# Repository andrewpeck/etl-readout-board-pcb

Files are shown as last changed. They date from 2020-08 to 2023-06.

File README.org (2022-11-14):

#+OPTIONS: ^:nil
#+EXPORT_EXCLUDE_TAGS: noexport
* CMS ETL Readout Board PCB :TOC:
  - [[#useful-links][Useful Links]]
  - [[#milestones][Milestones]]
  - [[#block-diagrams][Block Diagrams]]
  - [[#mechanical-outline][Mechanical Outline]]
  - [[#power][Power]]
  - [[#lpgbt-configuration][LPGBT Configuration]]
  - [[#vtrx-i2c][VTRX+ I2C]]
  - [[#v2-change-log][v2 Change Log]]
  - [[#errata][Errata]]

** Useful Links
- Documentation page: [[http://etl-rb.docs.cern.ch/][etl-rb.docs.cern.ch]]
- Latest RB Schematics - [[https://gitlab.cern.ch/cms-etl-electronics/readout-board-pcb/uploads/183954f3a47f967752902acf8ae9c3d3/ETL_RB_V1.6.PDF][ETL_RB_V1.6.PDF]]
- Latest RB Gerbers:  [[https://gitlab.cern.ch/cms-etl-electronics/readout-board-pcb/uploads/5678ebf45c38e1c627c98f56c8df58fa/ETL_RB_V1.6.zip][ETL_RB_V1.6.zip]]
- Latest RB Project Archive - [[https://gitlab.cern.ch/cms-etl-electronics/readout-board-pcb/uploads/25dc68e87a1a2c3de5a3411c434b7c02/ETL_RB__11-2-2020_9-17-11_AM_.zip][ETL_RB__11-2-2020_9-17-11_AM_.zip]]
- Mr. Wu's File Stash - [[http://physics.bu.edu/~wusx/download/ETL_RB/]]
- [[https://gitlab.cern.ch/vldbplus/rpi_translator_board_v2/-/raw/master/HW/Project%20Outputs%20for%20RPi_VLDB_Interface/v2-b/SCH/RPi_VLDB_Interface_v2b.PDF?inline=false][PiGBT Schematic]]

- Datasheets:
  + LpGBT Manual - [[https://lpgbt.web.cern.ch/lpgbt/manual/][LpGBT Manual]]
  + GBT-SCA Manual - [[https://espace.cern.ch/GBT-Project/GBT-SCA/Manuals/GBT-SCA_Manual_2019.002.pdf][GBT-SCA Manual]]
  + LINPOL12 Datasheet - [[https://project-dcdc.web.cern.ch/public/Documents/linPOL12V%20datasheetV3.3.pdf][LinPOL12V]]
  + VTRX+ Application Note: [[https://edms.cern.ch/ui/file/2149674/1/VTRxPlusApplicationNote.pdf][VTRxPlusApplicationNote.pdf]]
  + VTRX+ Specification: [[https://edms.cern.ch/ui/file/1719329/1/VTRxPlus_spec_v2.4.pdf][VTRxPlus_spec_v2.4.pdf]]
  + VTRX+ LDD Specs: [[https://edms.cern.ch/ui/file/1719330/1/VLplus_quadLDD_spec_v1.2_prototypes.pdf][VLplus_quadLDD_spec_v1.2_prototypes.pdf]]
- TDR - [[https://cds.cern.ch/record/2667167/files/CMS-TDR-020.pdf][CMS-TDR-020]]
** Milestones
- 2020/11/02 - Finish schematic and layout; Submit files to fab house
- 2020/12/08 - Receive readout boards from Pactron
- 2021/03/01 - Preliminary testing (LPGBT, elinks)
- 2021/03/18 - Working SCA GPIO Control
- 2021/03/23 - Working ADC voltage readings
- 2021/05/11 - 2nd batch of readout boards delivered to BU
- 2021/05/19 - Working SCA I2C master
** Block Diagrams
*** Data Flow
#+ATTR_HTML: :width 700px
[[file:docs/data-flow.svg]]
*** Module Connectivity
Full size: [[file:docs/module-connectivity.pdf]]
#+ATTR_HTML: :width 700px
[[file:docs/module-connectivity.svg]]
*** Power Distribution
#+ATTR_HTML: :width 700px
[[file:docs/power-distribution.svg]]
*** Control and Monitoring
#+ATTR_HTML: :width 700px
[[file:docs/ctrl-and-mon.svg]]
** Mechanical Outline
#+attr_org: :width 700px
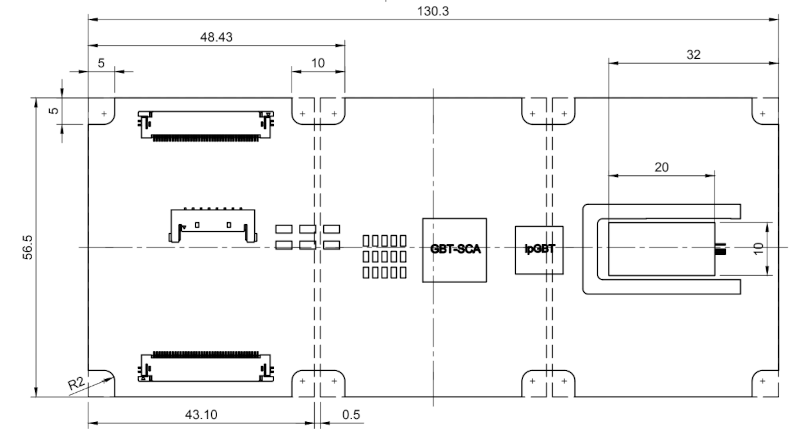
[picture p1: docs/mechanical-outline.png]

** Power
*** Power Estimates

The readout board is expected to dissipate up to ~1.3W, along with some
additional power for LINPOL conversion efficiency. Total power should be around
2W. Details of the calculation follow.

*NOTE:* This calculation is for a configuration of *2tx + 1rx* (i.e. with a trigger
path). The numbers are different if this is not the case (subtract roughly 0.6W
for the LPGBT/VTRX).

|-----------------------------+------------------|
| Note                        | P (mW)           |
|-----------------------------+------------------|
| 1.2V LPGBT analog + digital | 1000             |
| 1.2V VTRX digital           | 30               |
| 2.5V VTRX analog            | 150 - 175        |
| 1.5V GBT-SCA                | 65.4 - 108       |
| LINPOL12 Loss               | 613 - 853        |
|-----------------------------+------------------|
| *Total*                     | *1858 - 2166 mW* |
|-----------------------------+------------------|

**** VTRX
[[https://edms.cern.ch/ui/file/1719329/1/VTRxPlus_spec_v2.4.pdf][VTRX+ Specification]] specifies:
- A supply current 2V5RX of 40mA
- A supply current 2V5TX of  15/ch @ End of life (30mA for a 2+1 configuration)
- A supply current 1V2D of 5+10/ch mA (25mA for a 2+1 configuration)

|---------+--------+----------------+----------------------------------------|
| Voltage | I (mA) |         P (mW) | Notes                                  |
|---------+--------+----------------+----------------------------------------|
| 2V5RX   |     40 |            100 | 40mA total                             |
| 2V5TX   |  20-30 |          50-75 | 15mA/ch at end of life (10mA to start) |
| 1V2     |     25 |             30 | 5+10mA/ch                              |
|---------+--------+----------------+----------------------------------------|
| *Total* |        | *180 - 205 mW* |                                        |
|---------+--------+----------------+----------------------------------------|

**** GBT-SCA
The GBT-SCA manual specifies power consumption of:

|--------------------------------+-------------------+-----------------|
| Supply                         | Typical (Maximum) | Power mW        |
|--------------------------------+-------------------+-----------------|
| 1V5 VDD core                   | 36 (63) mA        | 54 (94.5) mW    |
| 1V5 AVDD analog                | 0.5 (0.8) mA      | 0.75 (1.2) mW   |
| 1V5 DVDD Static supply current | 7.1 (8.2) mA      | 10.65 (12.3) mW |
|--------------------------------+-------------------+-----------------|
| *Total*                          | *43.6 (72.0) mA*    | *65.4 (108.0) mW* |
|--------------------------------+-------------------+-----------------|

**** LPGBT
LPGBT power measurements can be found at
https://espace.cern.ch/GBT-Project/LpGBT/Presentations/lpGBT20190903.pdf

Note that these numbers may change between v0 and v1 of the LPGBT.

Power consumption is dependent on the exact configuration, but we expect it
should be <500mW

We expect up to 2 LPGBTs per board, so ~1W maximum.

**** LINPOL

Three LINPOL12 chips are used on board to provide 1.5V (GBT-SCA), and 2.5V (1
each for VTRX TX + RX).

For the 2.5V supply a voltage divider is formed by RR0510P-1541-D (1.54k) and
RR0510P-4870-D (487R).
 - V=0.6*(1+1540/487)=2.497V

For the 1.5V supply a voltage divider is formed by RR0510P-6040-D (604R) and
RR0510P-4020-D (402R).
 - V= 0.6*(1+604/402)=1.50V

We have some additional power loss in the LINPOL12 chips, which is dependent on
the exact input voltage. Assuming 8V nominal, we would expect using the /MAXIMUM/
values:

|--------+-------------------------------------------|
| Supply | Power mW                                  |
|--------+-------------------------------------------|
| 1V5    | (8-1.5)*(43.6 - 72) = (283 typ - 468 max) |
| 2V5 TX | (8-2.5)*(20 - 30) = (110 start - 165 EOL) |
| 2V5 RX | (8-2.5)*40 = 220                          |
|--------+-------------------------------------------|
| *Total*  | *613 - 853 mW*                              |
|--------+-------------------------------------------|

** LPGBT Configuration

The DAQ and Trigger LPGBTs are arranged in a master-slave configuration, with
the master LPGBT providing a clock and an I2C bus to the slave.

Both LPGBTs are configured by default in FEC12 10.24 Gbps mode, with jumpers
available to select FEC5 or 5.12 Gbps modes. CHange of the mode affects both
LPGBTs together.

|---------+--------------------------------------------------------|
| Jumpers | Description                                            |
|---------+--------------------------------------------------------|
| JMP1    | Install to set LPGBT MODE[2] to 0 (FEC12 → FEC5)       |
| JMP2    | Install to set LPGBT MODE[3] to 0 (data rate → 5 Gbps) |
|---------+--------------------------------------------------------|

** VTRX+ I2C
VTRX+ documentation does not specify the I2C address of the device, but the
laser driver spec has some details:
[[https://edms.cern.ch/ui/file/1719330/1/VLplus_quadLDD_spec_v1.2_prototypes.pdf]]

I checked the bonding diagram
([[https://edms.cern.ch/ui/file/2146792/1/CERN_VTRxPlus_V10_bonding.pdf]]) and the
address pins are not connected, so they use internal pull down.

The address then is ~0b1010000~ = ~0x50~

** v2 Change Log
- [X] Replace KSC2223 BJT w/ ZXMN2B01FTA
- [X] Parallelized LinPol Outputs for higher output current
- [X] Fix I2C note
- [X] Remove I2C programmer port / EFUSEPOWER
- [X] PB and BV interfaces removed
  - Connections can be made as needed directly on the breakout board
- [X] Addition of LEDs
  + [X] Master and slave READY signals connected to LEDs
  + [X] Connect power to LED
  + [X] Connect LPGBT GPIO to LED
  + [X] Connect SCA GPIO to LED
- [X] lpGBT v1 Changes:
  + [X] SC_I2C changed to BOOTCNF1, Should be tied to 0 (https://lpgbt.web.cern.ch/lpgbt/v1/powerup.html#bootcnf1-bootcnf0)
  + [X] Stateovrd changed to EDINTERM
    - "Notice that pin EDINECTERM contains a pull-down resistor. If left
      unconnected, the eRx termination for the EC channel will be disabled.
      Notice as well, that this pin has no effect when the lpGBT is set to work
      as a transceiver. In that case, it is the responsibility of the user to
      configure the termination for the EC-channel in master lpGBTs."
    - https://lpgbt.web.cern.ch/lpgbt/v1/configuration.html?highlight=edinecterm#ec-channel-control-link-topologies
  + [X] VCOBypass changed to BOOTCNF0
    - https://lpgbt.web.cern.ch/lpgbt/v1/powerup.html#bootcnf1-bootcnf0
    - Need to be able to change from 0 <--> 1 to select boot mode
- [X] Latest module pinout (monitor 1x VREF and VTEMP per ETROC)
- [X] Update module connector (QSE-020-01-F-D)
  + RB side: QSE-020-01-{F,L,C}-D
  + Mating connector QTE-020-01-{F,L,C}-D
  + Test report: https://suddendocs.samtec.com/testreports/168830_report_rev_6_qua.pdf
  + 5mm stack height with QTE lead style -01
  + Catalog page: https://suddendocs.samtec.com/catalog_english/qse.pdf
** Errata
1) KSC2223 footprint is incorrect
   - The footprint of the KSC2223 transistor is incorrect.
2) Incorrect assignment of e-fuse power
   - EFUSEPOWER (2.5V power to be applied only during fusing) is incorrectly
     connected to I2C configuration connector ~P1~, pin 9. Pin 9 is in fact the
     ~MODE3_1V25~ pin of the Rpi control toolkit, and should /not/ be connected to
     EFUSE power.
   - *The trace must be cut*.
3) Erroneous note about I2C addresses
   - The schematic features a note:
#+begin_src
I2C ADDR6, ADDR5 and ADDR4 of ETROC2 must not be all 0 or all 1.
pin 11 of P6, P8 and P10 sets ADDR2 of ETROC2
pin 12 of P6, P8 and P10 sets ADDR3 of ETROC2
#+end_src
     + This note, is, however, a remnant of a previous iteration of the design
       where all modules were on the same i2c bus. In the current configuration,
       each module has its own I2C bus, and shares the same address.

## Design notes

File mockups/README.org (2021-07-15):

* Adapters & Mockup Files
** Power adapter
- [[file:power_adapter/v1_power_adapter.pdf][Schematic]]
- [[file:power_adapter/gerber/v1_power_adapter_gerber_20200714.zip][v1_power_adapter_gerber_20200714.zip]]
#+attr_org: :width 300px
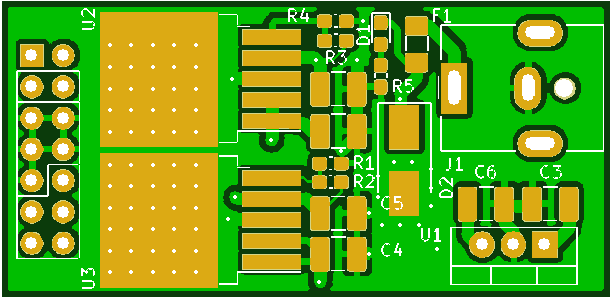
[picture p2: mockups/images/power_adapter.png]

** Emulator Adapter
Adapter board to connect to the ETROC emulator.
- [[file:adapterv1.0.zip][adapterv1.0.zip]]
#+attr_org: :width 500px
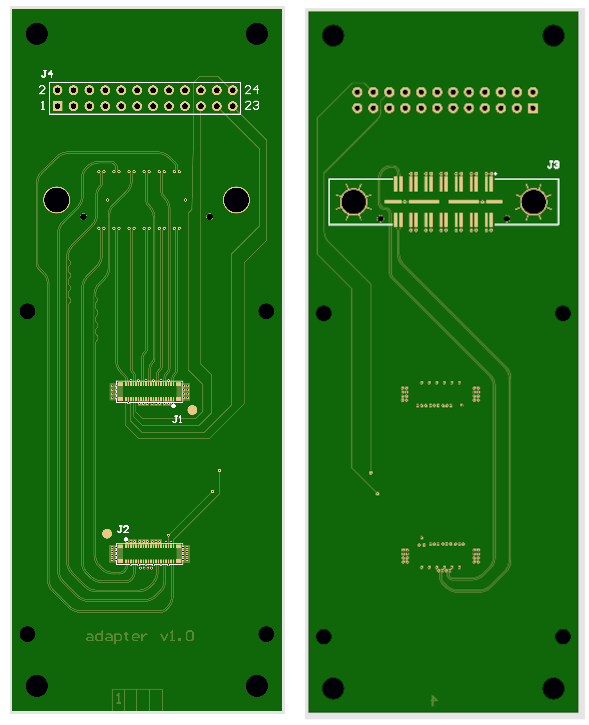
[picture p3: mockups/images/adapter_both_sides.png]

** [[file:ETL_RB_mock1v2.zip][ETL_RB_mock1v2.zip]]
Mockup of a 3 module readout board with realistic pad connectivity
#+attr_org: :width 600px
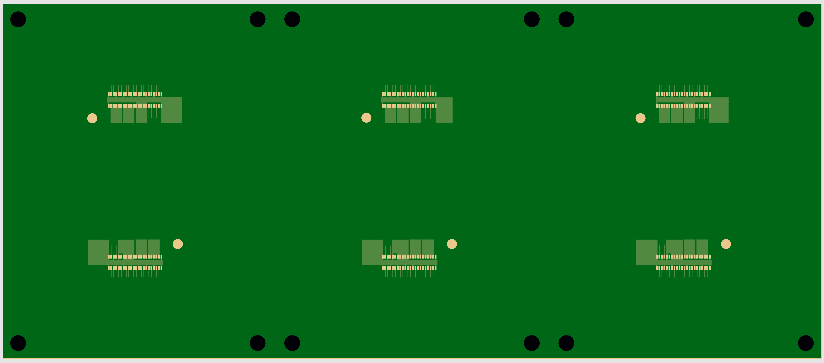
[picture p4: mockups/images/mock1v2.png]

** [[file:ETL_RB_mock2v2.zip][ETL_RB_mock2v2.zip]]
Mockup of a 3 module readout board with daisy-chain connectivity
#+attr_org: :width 600px
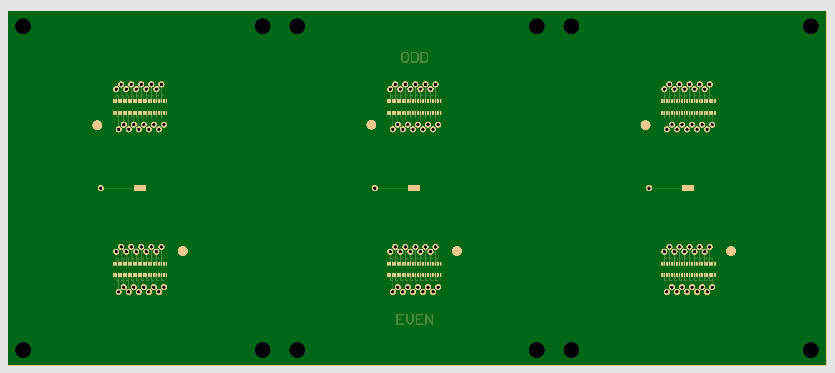
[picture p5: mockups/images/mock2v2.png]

** [[file:module_mockv3.zip][module_mockv3.zip]]
Mockup of a full-sized module (2 sensors, 4 etrocs) with daisy-chain connectivity
#+attr_org: :width 200px
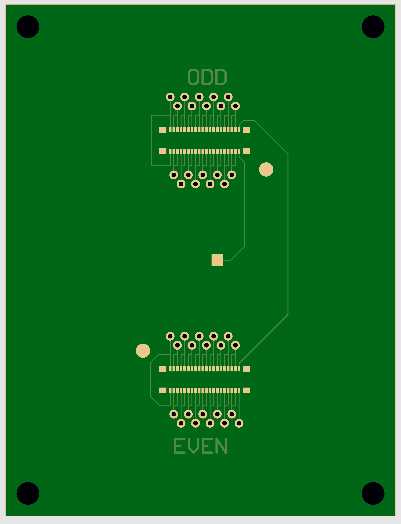
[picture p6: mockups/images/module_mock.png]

** [[file:ETL_BKv2.zip][ETL_BKv2.zip]]
Module-like breakout board
#+attr_org: :width 200px
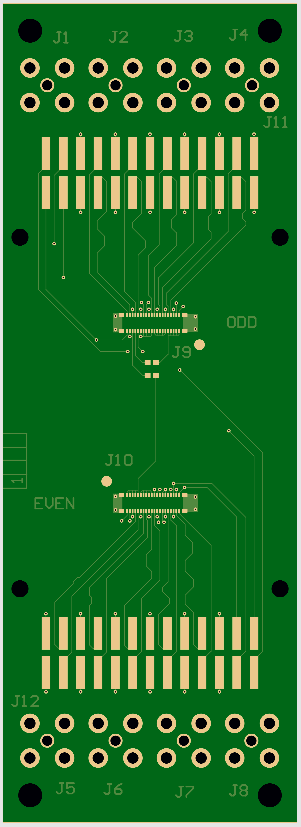
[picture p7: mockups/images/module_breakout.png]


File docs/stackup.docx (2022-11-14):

PCB Stack Up | | | | | | | Impedance
Layer | Type | | Thickness (mil) | | | DK/DF | Single end
Top side solder mask | | | | 0.70 | mils | 4.1/0.022 | LINE(mil) | Reference | ohm | TheoryValue
L1 | TOP | Signal | copper+plating | 1.6 | mils | | 4.00→4.50 | L2 | 50 | 50.92
| | TU-863P | 1080 63% | 2.72 | mils | 3.4/
L2 | | Signal | copper | 1.4 | mils
| | TU-863 substrate | core | 4 | mils | 3.7/
L3 | | Signal | copper | 0.7 | mils | | 4.00→4.50 | L2/L4 | 50 | 49.71
| | TU-863P TU-863P | 1080 63% 1080 63% | 5.58 | mils | 3.40/0.0000
L4 | | Signal | copper | 1.4 | mils
| | TU-863 substrate | core | 4 | mils | 3.7/
L5 | | Signal | copper | 1.4 | mils
| | TU-863P TU-863P | 1080 63% 1080 63% | 5.58 | mils | 3.40/0.0000
L6 | | Signal | copper | 0.7 | mils | | 4.00→4.50 | L5/L7 | 50 | 49.71
| | TU-863 substrate | core | 4 | mils | 3.7/
L7 | | Signal | copper | 1.4 | mils
| | TU-863P | 1080 63% | 2.72 | mils | 3.4/0
L8 | Bottom | Signal | copper+plating | 1.6 | mils | | 4.00→4.50 | L7 | 50 | 50.92
Bottom side solder mask | | | | 0.70 | mils | 4.1/0.022
TOTAL | | | | 40.20 | mils
| | | | 1.02 | mm

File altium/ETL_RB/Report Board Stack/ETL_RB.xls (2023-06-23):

Board Stack Report
Stack Up |  | Layer Stack
Layer | Board Layer Stack | Name | Material | Thickness | Constant
1 |  | Top Paste
2 |  | Top Overlay
3 |  | Top Solder | Solder Resist | 0.018mm | 4.1
4 |  | Top Layer | Copper | 0.018mm
5 |  | Dielectric 1 | 1080 | 0.069mm | 3.4
6 |  | plane 1 | Copper | 0.035mm
7 |  | Dielectric 2 | TU-863 | 0.102mm | 3.7
8 |  | M1 | Copper | 0.018mm
9 |  | Dielectric 3 | 1080 | 0.142mm | 3.4
10 |  | plane 2 | Copper | 0.035mm
11 |  | Dielectric 4 | TU-863 | 0.102mm | 3.7
12 |  | plane 3 | Copper | 0.035mm
13 |  | Dielectric 5 | 1080 | 0.142mm | 3.4
14 |  | M2 | Copper | 0.018mm
15 |  | Dielectric 6 | TU-863 | 0.102mm | 3.7
16 |  | plane 4 | Copper | 0.035mm
17 |  | Dielectric 7 | 1080 | 0.069mm | 3.4
18 |  | Bottom Layer | Copper | 0.018mm
19 |  | Bottom Solder | Solder Resist | 0.018mm | 4.1
20 |  | Bottom Overlay
21 |  | Bottom Paste
 | Height : 0.973mm

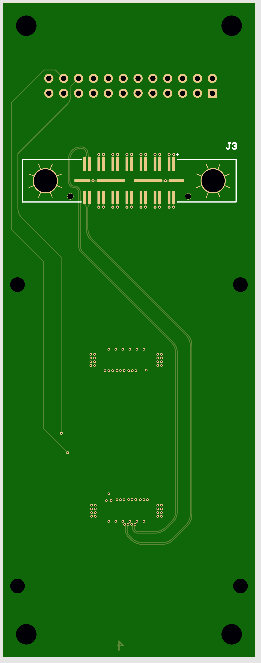
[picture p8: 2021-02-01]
mockups/images/adapter_bottom.png

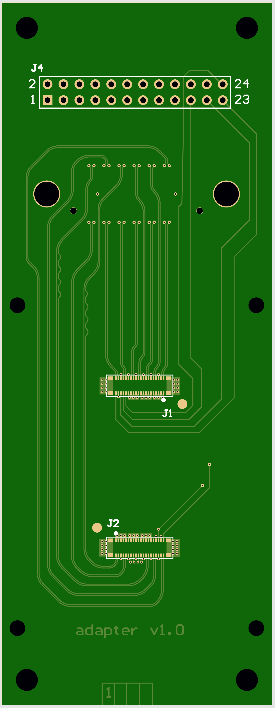
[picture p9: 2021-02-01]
mockups/images/adapter_top.png

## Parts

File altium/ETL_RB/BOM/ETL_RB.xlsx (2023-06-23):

Comment | Description | Designator | Footprint | LibRef | Quantity
GRM185R60J106ME15J | CERAMIC CAPACITOR | C1, C2, C108, C169 | CAPC1608N | C | 4
GRM155R71E104ME14D | CERAMIC CAPACITOR | C3, C4, C5, C6, C7, C8, C9, C10, C11, C12, C13, C14, C16, C17, C18, C19, C20, C21, C22, C23, C24, C25, C26, C27, C28, C29, C30, C31, C32, C106, C150, C151, C152, C153, C154, C160, C201 | capc1005n | C | 37
GRM188R60J476ME15D | CERAMIC CAPACITOR | C111, C112, C127, C162 | capc2012n | C | 4
GRM033R61C104KE84D | CERAMIC CAPACITOR | C113, C114, C115, C116, C117, C118, C119, C120, C121, C128, C129, C130, C131, C132, C133, C134, C135, C163 | capc0603n | C | 18
GRM033R61C153KE84D | CERAMIC CAPACITOR | C122, C123, C124, C125, C126, C164, C165, C166, C167, C168 | capc0603n | C | 10
LTST-C191KRKT | Typical RED, GREEN, YELLOW, AMBER GaAs LED | D1, D7 | LED_RED | LED_RED | 2
LTST-C191KGKT | Typical RED, GREEN, YELLOW, AMBER GaAs LED | D2, D3 | LED_RED | LED_GREEN | 2
LPGBT | Low Power Gigabit Transceiver | IC1, IC4 | BGA289X17 | LPGBT | 2
DF40C-40DS-0.4V | VTRX+ module with 2.5mm stack Height. | IC2 | vtrx+ | VTRX+_DF40C-2.0-40DS-0.4V | 1
linPOL12V |  | IC6, IC7 | WDFNX208 | linPOL12V | 2
QSE-020-01-XXX-D | 40 Position Connector Receptacle, Center Strip Contacts Surface Mount Gold | J1, J2, J3, J4, J5, J6 | SAMTEC_QSE-020-01-XXX-D | QSE-020-01-XXX-D | 6
U.FL-R-SMT(01) | CONN U.FL RCPT STR 50 OHM SMD | J7, J8 | U.FL-R-SMT(01) | U.FL-R-SMT(01) | 2
SBH11-PBPC-D07-ST-BK | Connector | J9 | SHDR14W64P254_2X7_2528X910X910P | SBH11-PBPC-D07-ST-BK | 1
ZXMN2B01FTA | MOSFET N-CH 20V 2.1A SOT-23-3 | Q1, Q2, Q6 | SOT-23 | ZXMN2B01FTA | 3
ERJ-2GEJ102X | FILM RESISTOR | R1, R2, R3, R142 | resc1005n | R1 | 4
0R | FILM RESISTOR | R4, R9 | R0805 | R1 | 2
DNP | FILM RESISTOR | R5, R10 | R0805 | R1 | 2
ERJ-2BQJR30X | FILM RESISTOR | R6, R11, R114, R125 | resc1005n | R1 | 4
RR0510P-4870-D | FILM RESISTOR | R7, R12, R115, R123 | resc1005n | R1 | 4
RR0510P-1541-D | FILM RESISTOR | R8, R13, R116, R124 | resc1005n | R1 | 4
ERJ-2GEJ392X | FILM RESISTOR | R14, R15, R101, R103, R104, R105, R106 | resc1005n | R1 | 7
82Kohm | FILM RESISTOR | R16, R20, R22, R24, R26, R29, R32, R35 | resc1005n | R1 | 8
RR0510P-103-D | FILM RESISTOR | R17 | resc1005n | R1 | 1
120Kohm | FILM RESISTOR | R18, R21, R23, R25, R27 | resc1005n | R1 | 5
RR0510P-102-D | FILM RESISTOR | R19 | resc1005n | R1 | 1
3.9k | FILM RESISTOR | R28 | resc1005n | R1 | 1
HVC1206T5005JET | FILM RESISTOR | R30, R31, R33, R34, R36, R37 | resc3216n | HVC1206T5005JET | 6
1.2Kohm | FILM RESISTOR | R38, R40, R42, R44 | resc1005n | R1 | 4
3.2Kohm | FILM RESISTOR | R39, R41, R43, R45 | resc1005n | R1 | 4
RR0510P-302-D | FILM RESISTOR | R119, R135 | resc1005n | R1 | 2
RR0510P-152-D | FILM RESISTOR | R120, R122 | resc1005n | R1 | 2
ERJ-2GEJ5R1X | FILM RESISTOR | R130, R131 | resc1005n | R1 | 2
ERJ-1GEF4023C | FILM RESISTOR | R146 | resc0603 | R1 | 1
ERJ-1GNF1004C | FILM RESISTOR | R147 | resc0603 | R1 | 1
ERJ-2RKF4751X | FILM RESISTOR | R148 | resc1005n | R1 | 1
NTCG063UH103HTBX | Thermistor | RT1 | resc0603 | Res Thermal | 1
MUX64 |  | U1 | QFN40P1000X1000X80_HS-89N | MUX64 | 1

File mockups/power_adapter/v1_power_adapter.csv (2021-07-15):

Reference | Quantity | Value | Footprint | Datasheet | PN
C1 C4 C5 C2 C3 C6 C7 | 7 | 47uF | Capacitor_SMD:C_1210_3225Metric_Pad1.42x2.65mm_HandSolder | ~ | GRM32ER61C476ME15L
D1 | 1 | LED | LED_SMD:LED_0603_1608Metric_Pad1.05x0.95mm_HandSolder | ~ | LTST-C193KRKT-5A
D2 | 1 | 10V | Diode_SMD:D_SMB_Handsoldering | ~ | 3SMBJ5925B-TP
F1 | 1 | Fuse | Fuse:Fuse_1206_3216Metric_Pad1.42x1.75mm_HandSolder | ~ | 1206L035/30WR
J1 | 1 | Barrel_Jack | Connector_BarrelJack:BarrelJack_CUI_PJ-063AH_Horizontal | ~ | PJ-063AH
J2 | 1 | Conn_02x07_Odd_Even | Connector_PinSocket_2.54mm:PinSocket_2x07_P2.54mm_Vertical | ~ | SFH11-PBPC-D07-ST-BK
R1 | 1 | 1G | Resistor_SMD:R_0603_1608Metric_Pad1.05x0.95mm_HandSolder | ~
R2 | 1 | 0 | Resistor_SMD:R_0603_1608Metric_Pad1.05x0.95mm_HandSolder | ~ | RMCF0603ZT0R00
R3 | 1 | 5.1k | Resistor_SMD:R_0603_1608Metric_Pad1.05x0.95mm_HandSolder | ~ | RMCF0603FT5K10
R5 R4 | 2 | 1k | Resistor_SMD:R_0603_1608Metric_Pad1.05x0.95mm_HandSolder | ~ | RMCF0603JT1K00
U1 | 1 | L7805 | Package_TO_SOT_THT:TO-220-3_Vertical | http://www.st.com/content/ccc/resource/technical/document/datasheet/41/4f/b3/b0/12/d4/47/88/CD00000444.pdf/files/CD00000444.pdf/jcr:content/translations/en.CD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 | TPSM84203EAB
U3 U2 | 2 | LT1963EQ | Package_TO_SOT_SMD:TO-263-5_TabPin3 | https://www.analog.com/media/en/technical-documentation/data-sheets/1963fc.pdf | LT1963EQ#TRPBF

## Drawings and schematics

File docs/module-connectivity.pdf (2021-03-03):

Module 1 | Module 2 | Module 3

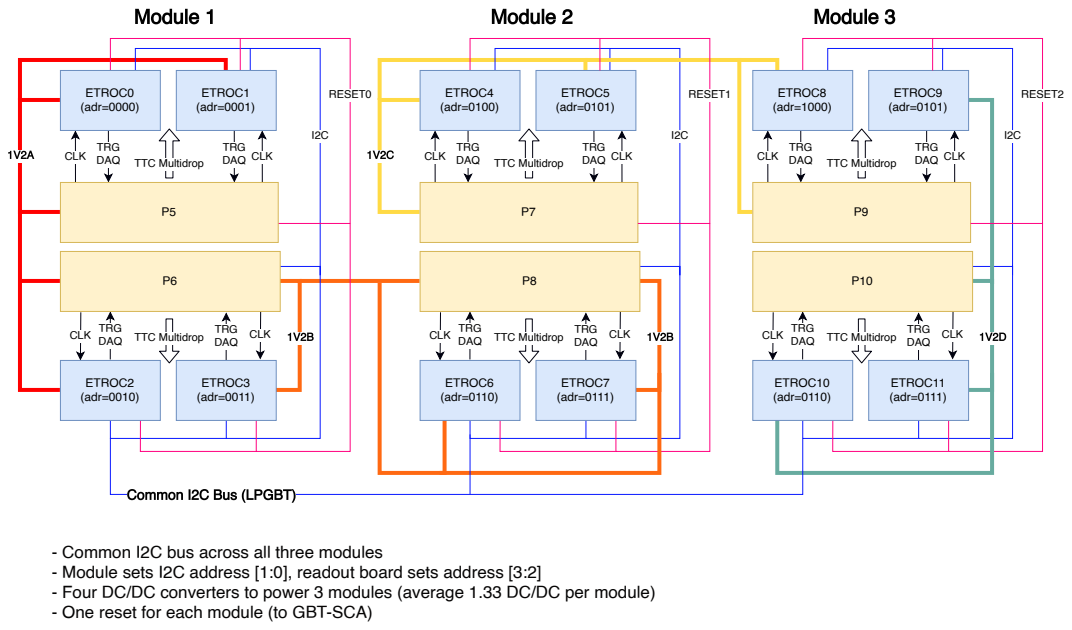
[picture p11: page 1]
CLK; TRG DAQ; TRG; TTC Multidrop; DAQ; CLK TRG; RESET0; ETROC6 (adr=0110); ETROC5 (adr=0101); ETROC7 (adr=0111); ETROC4 (adr=0100); ETROC2 (adr=0010); ETROC1 (adr=0001); ETROC3 (adr=0011); ETROC0 (adr=0000); ETROC10 (adr=0110); ETROC9 (adr=0101); ETROC11 (adr=0111); ETROC8 (adr=1000); RESET1; RESET2

DAQ CLK TRG
DAQ

Common I2C Bus (LPGBT)

- Common I2C bus across all three modules
- Module sets I2C address [1:0], readout board sets address [3:2]
- Four DC/DC converters to power 3 modules (average 1.33 DC/DC per module)
- One reset for each module (to GBT-SCA)

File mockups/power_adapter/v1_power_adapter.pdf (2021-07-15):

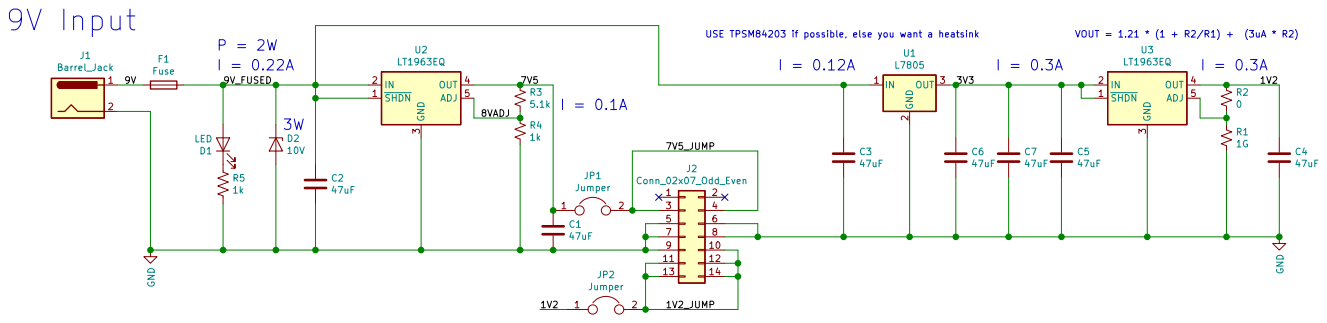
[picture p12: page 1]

USE TPSM84203 if possible, else you want a heatsink

File: v1_power_adapter.sch Sheet: / Boston University GND

Id: 1/1 Title: ETL Readout Board Power Adapter

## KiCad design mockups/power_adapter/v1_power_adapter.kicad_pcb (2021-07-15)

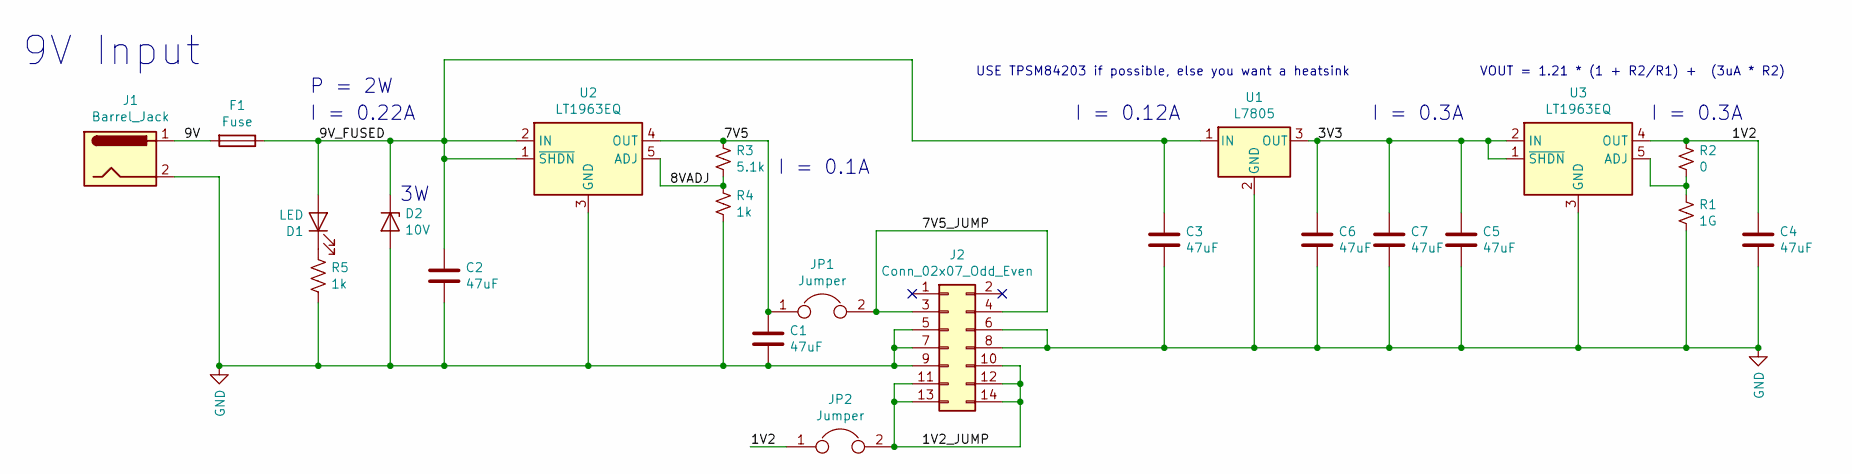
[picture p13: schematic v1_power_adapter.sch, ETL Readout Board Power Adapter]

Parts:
C1, C2, C3, C4, C5, C6, C7: 47uF; C_1210_3225Metric_Pad1.42x2.65mm_HandSolder
D1: LED; LED_0603_1608Metric_Pad1.05x0.95mm_HandSolder
D2: 10V; D_SMB_Handsoldering
F1: Fuse; Fuse_1206_3216Metric_Pad1.42x1.75mm_HandSolder
J1: Barrel_Jack; BarrelJack_CUI_PJ-063AH_Horizontal
J2: Conn_02x07_Odd_Even; PinSocket_2x07_P2.54mm_Vertical
JP1, JP2: Jumper; PinHeader_1x02_P2.54mm_Vertical
R1: 1G; R_0603_1608Metric_Pad1.05x0.95mm_HandSolder
R2: 0; R_0603_1608Metric_Pad1.05x0.95mm_HandSolder
R3: 5.1k; R_0603_1608Metric_Pad1.05x0.95mm_HandSolder
R4, R5: 1k; R_0603_1608Metric_Pad1.05x0.95mm_HandSolder
U1: L7805; TO-220-3_Vertical
U2, U3: LT1963EQ; TO-263-5_TabPin3

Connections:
/1V2: C4.1, JP2.1, R2.1, U3.4 (OUT)
/1V2_JUMP: J2.10, J2.11, J2.12, J2.13, J2.14, JP2.2
/3V3: C5.1, C6.1, C7.1, U1.3 (OUT), U3.1 (~SHDN), U3.2 (IN)
/7V5: C1.1, JP1.1, R3.1, U2.4 (OUT)
/7V5_JUMP: J2.3, J2.4, JP1.2
/8VADJ: R3.2, R4.1, U2.5 (ADJ)
/9V: F1.2, J1.1
/9V_FUSED: C2.1, C3.1, D1.2 (A), D2.1 (K), F1.1, U1.1 (IN), U2.1 (~SHDN), U2.2 (IN)
GND: C1.2, C2.2, C3.2, C4.2, C5.2, C6.2, C7.2, D2.2 (A), J1.2, J2.5, J2.6, J2.7, J2.8, J2.9, R1.2, R4.2, R5.2, U1.2 (GND), U2.3 (GND), U3.3 (GND)
unnamed: D1.1 (K), R5.1
unnamed: R1.1, R2.2, U3.5 (ADJ)

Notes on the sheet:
USE TPSM84203 if possible, else you want a heatsink
VOUT = 1.21 * (1 + R2/R1) + (3uA * R2)
9V Input
I = 0.3A
I = 0.1A
I = 0.12A
I = 0.22A
P = 2W

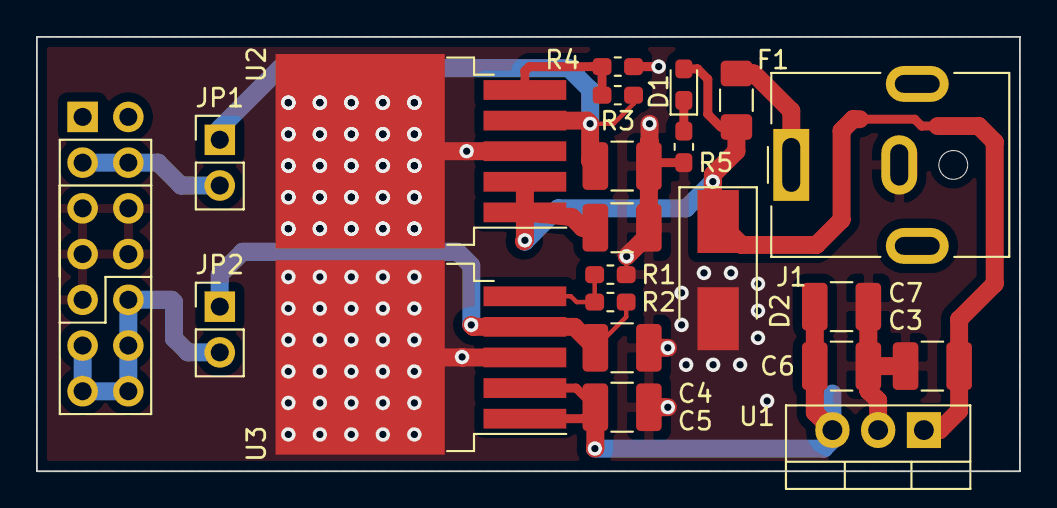
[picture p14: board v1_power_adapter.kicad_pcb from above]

Board: 2 copper layers, 54.6 x 24.1 mm, 22 parts (1 on the bottom side), 11 nets.

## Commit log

2020-09-01 Add altium files
    [ETL_RB.PcbDoc, ETL_RB.PrjPcb, HEP_DEV.SchLib, lpGBT.SchDoc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]
2020-09-04 PCB updates from Mr. Wu
    [ETL_RB.PcbDoc, ETL_RB.PrjPcb, lpGBT.SchDoc]
2020-09-09 9/20/2020 version from Mr. Wu
    [ETL_RB.PcbDoc, ETL_RB.PrjPcb, lpGBT.SchDoc]
2020-09-11 Updates from Mr. Wu
    [ETL_RB.PcbDoc, ETL_RB.PrjPcb, lpGBT.SchDoc]
2020-09-11 Updates from 2020/09/11
    - Resistor values of voltage divider for ADC input reduced to keep impedance less than 1K
    - 1V2_RB input for ADC removed as lpGBT has internal channels for that already.
    [ETL_RB.PrjPcb, lpGBT.SchDoc]
2020-09-15 Add missing file
    [ETL_RB.PrjPcb, WP7B.SchDoc]
2020-09-24 Updates from 20200916
    [ETL_RB_v1.3.PcbDoc]
2020-10-26 Replace connectors with simple headers
    [ETL_RB.PrjPcb, WP7B.SchDoc, lpGBT.SchDoc]
2020-11-02 v1.6 Update from Mr. Wu
    - I just made some changes on the RB layout to make v1.6 It occurred to me that the current I2C bus has a problem that if one sensor module is bad, it can hold the all three modules dead.
    - This means we need eventually use GBT-SCA for I2C control.
    - So we need to make sure I2C masters of GBT-SCA is compatible with ETROC, so I changed two sensor modules I2C to GBT-SCA I2C masters.
    - I hope this is not going to change the quote as this is only a minor change.
    - Just want to let you know so that they don't start the production of v1.5 now.
    [ETL_RB.PcbDoc, ETL_RB.PrjPcb, ETL_RB_v1.3.PcbDoc, WP7B.SchDoc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]
2020-11-10 WP7B connectors' center groud strip width changed from 1mm to 0.8mm as recommended in its datasheet.
    [ETL_RB.PcbDoc, ETL_RB.PrjPcb, WP7B.SchDoc, lpGBT.SchDoc]
2021-02-01 Add adapter board files
2021-07-15 Add power adapter files
    [v1_power_adapter.csv, v1_power_adapter.kicad_pcb, v1_power_adapter.sch]
2021-07-15 Use grouped CSV
    [v1_power_adapter.csv]
2021-07-15 Add jumpers for current measurement
    [v1_power_adapter.kicad_pcb, v1_power_adapter.sch]
2022-07-26 Fix altium project
    [ETL_RB.PrjPcb, WP7B.SchDoc, lpGBT.SchDoc]
2022-11-10 New version of ETL
    [ETL_RB.PcbLib, ETL_RB.PrjPcb, ETL_RB.SCHLIB, LINPOL12.SchDoc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]
2022-11-10 Re-commiting project
    [HEP_DEV.SchLib, lpgbt.SchLib]
2022-11-11 updated project fixings errors
    [ETL_RB.PcbLib, ETL_RB.SCHLIB, LINPOL12.SchDoc, Power.SchDoc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]
2022-11-14 update date / version in schematic
    also update outjob
    [ETL_RB.PrjPcb, ETL_RB.SCHLIB, LINPOL12.SchDoc, Power.SchDoc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]
2022-11-30 Fixing internal plane
    [ETL_RB.PrjPcb]
2023-01-03 Add new emulator adapter design
    [emulator_adapter.PcbDoc, emulator_adapter.SchDoc, emulator_adapter_v2.PrjPcb]
2023-01-03 Add test stand baseplate files
    [test_stand_base.PcbDoc, test_stand_plate.PrjPcb]
2023-01-03 Add rb mockup files
    [ETL_RB.PcbLib, ETL_RB.SCHLIB, ETL_RB.SchDoc, ETL_RB_Mockup.PcbDoc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]
2023-01-03 Add v3 RB mockup files
    [ETL_RB.PcbDoc, ETL_RB.PcbLib, ETL_RB.SCHLIB, ETL_RB.SchDoc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]
2023-01-03 Add date to emulator adapter pcb
    [emulator_adapter.PcbDoc]
2023-01-03 length matching for emulator board
    [emulator_adapter.PcbDoc, emulator_adapter_v2.PrjPcb]
2023-06-12 Add footprint and schematic symbol for mux64
    [ETL_RB.PcbLib, ETL_RB.SCHLIB]
2023-06-14 updated SDA and SCL on RB connectors to be uniform
    [WP7B.SchDoc]
2023-06-14 Removed 1V5A and 1V4D test points, pull up resistors from SDA1/SDA2,and sca_led
    [WP7B.SchDoc]
2023-06-14 removed 1V5A and 1V4D voltage dividers
    [WP7B.SchDoc, lpGBT.SchDoc]
2023-06-14 removed 1V5 test point and linPOL12V which created 1V5A and 1V4D
    [LINPOL12.SchDoc]
2023-06-14 removed GBT-SCA that was powered by 1V5A and 1V4D
    [Power.SchDoc]
2023-06-14 saved doc
    [LINPOL12.SchDoc]
2023-06-14 updated MUX64 schematic symbol to better match current schematic colors
    [ETL_RB.SCHLIB, LINPOL12.SchDoc, Power.SchDoc, WP7B.SchDoc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]
2023-06-14 replaces SCA with MUX64
    [WP7B.SchDoc]
2023-06-14 Added a note to last remaining SCA on page
    [WP7B.SchDoc]
2023-06-14 added power and ground to MUX64
    [WP7B.SchDoc]
2023-06-15 Save current project files
    [ETL_RB.PrjPcb]
2023-06-15 moved testpoints
    [LINPOL12.SchDoc]
2023-06-15 craeted pdf of schematic
    [ETL_RB.PrjPcb]
2023-06-20 saving pervious session comments
    [WP7B.SchDoc, lpGBT.SchDoc]
2023-06-20 Added select pins and removed SCA connected to master
    [WP7B.SchDoc, lpGBT.SchDoc]
2023-06-20 added Mod and WS reset
    [WP7B.SchDoc]
2023-06-20 Copied Linpol12 sheet to make powerboard connector
    [ETL_RB.PrjPcb, PowBoardConn.SchDoc]
2023-06-20 Added Pgood and P_enable on servant gpio
    [PowBoardConn.SchDoc, lpGBT.SchDoc]
2023-06-20 added PTAT signals as inputs to MUX64
    [PowBoardConn.SchDoc, WP7B.SchDoc]
2023-06-20 updated project structure
    [ETL_RB.PrjPcb]
2023-06-20 added voltage divider to MUX64 PTAT inputs
    [ETL_RB.PrjPcb, WP7B.SchDoc]
2023-06-20 Created pdf of current schematic
    [ETL_RB.PrjPcb]
2023-06-22 removed SCA and renamed module digital and analog pins. Also reorganized MUX64 connections
    [WP7B.SchDoc]
2023-06-22 Annoted changed and created pdf
    [WP7B.SchDoc]
2023-06-22 format change
    [WP7B.SchDoc]
2023-06-22 added 1V2 PB monitoring channels to MUX64
    [PowBoardConn.SchDoc, WP7B.SchDoc]
2023-06-23 Added BV signals to MUX64
    [PowBoardConn.SchDoc, WP7B.SchDoc]
2023-06-23 Update outjob
    [ETL_RB.PrjPcb]
2023-06-23 added outjob and minor fixes to schematic
    [ETL_RB.GBL, ETL_RB.GBO, ETL_RB.GBP, ETL_RB.GBS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]
2023-06-23 remade schematic pdf and gerber files
    [ETL_RB.GBL, ETL_RB.GBO, ETL_RB.GBP, ETL_RB.GBS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]
2023-06-23 fixed minor errors
    [WP7B.SchDoc]
2023-06-23 renamed tag to Servant
    [lpGBT.SchDoc]
2023-06-23 regenerated pdf and gerber files
    [ETL_RB.GBL, ETL_RB.GBO, ETL_RB.GBP, ETL_RB.GBS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]
